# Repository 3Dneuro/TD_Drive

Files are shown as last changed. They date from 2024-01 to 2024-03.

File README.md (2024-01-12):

# TD Drive
Here, we present a novel, 3D-printable implant for rats, named TD Drive, capable of symmetric, bilateral wire electrode recordings, currently in up to six distributed brain areas simultaneously. The open-source design was created employing parametric design principles, allowing prospective users to easily adapt the drive design to their needs by simply adjusting high-level parameters, such as anterior-posterior and medio-lateral coordinates of the recording electrode locations.

We set out to create an easily adjustable hyperdrive to aid neuroscientists in overcoming the difficulties brought about by the multi-area nature of brain interactions. This is one of the main obstacles faced by researchers aiming to exhaustively study the ongoing physiological processes in the brain during both wakefulness and sleep. To capture them accurately, extracellular electrophysiology, recorded with electrodes implanted in the brain areas of interest, is one of methods of choice due to its high temporal resolution and spatial precision.

Classically, studies recording brain activity with extracellular electrodes have employed individual wire electrodes or electrode bundles, such as tetrodes. State-of-the-art probes such as the Neuropixels probe allow the targeting of several areas simultaneously, given that they are aligned on an axis that does allow for implantation of the probe along that axis without impairing the animal. However, accurate simultaneous recordings of multiple, spatially separated areas still remain challenging, with existing methods being either costly or time intensive. 

To make this kind of research more accessible to the scientific community, we set out to create a hyperdrive design that can be modified by individual users, all while being producible in-house. The TD Drive thus aims to overcome some of the drawbacks of existing solutions: it allows targeting of multiple brain areas, mirrored across both hemispheres, with independent wire electrodes simultaneously. Due to its simple design, it can be assembled in a few hours at a relatively low cost. We publish the TD Drive open source, in easily modifiable file formats, to allow researchers to adjust it to their specific needs. A protective cap and electrode interface board (EIB), both available in a standard and enlarged version, complete the experimental framework. The enlarged versions provide increased freedom to make parametric changes to the drive body. Incorporating a parametric 3D modeling approach from the beginning of the TD Drive’s design process allowed us to abstract the parameters necessary to be changed: to change target locations, researchers can simply edit the parameters representing their dorsoventral and anteroposterior coordinates, without the need for redesigning the drive themselves.

Parametric feature demonstration default Parametric feature demonstration alternate

# Parameters
*The parametric design was created in Autodesk Fusion 360. To edit the parameters described below, you will need to import the f3d file into Fusion 360. At time of publication, a free Fusion 360 license for academics/educators was available from Autodesk.*

The TD Drive was designed using a parametric modeling approach. In this process, popular in computer-aided design, different components of the design are linked by interdependent parameters and a defined design history. The design can be altered to suit your needs by modifying the parameters controlling the relevant dimensions. This eliminates the need for researchers to redesign the model themselves, with simple changes to the high-level parameters taking care of all the desired design modifications.

Apart from changing dimensions of the design, the parametric functionality is also used to provide the option to bilaterally add a set of fibers to the body. To make opting in and out of adding the fibers depending on your experimental needs as simple as possible, a custom-made plugin (hyperlink) for Fusion 360 is provided. With use of this plugin, the suppression of all design features pertaining to the fibers can be toggled with the use of a single parameter.

The table below contains the parameter names, a description of their function and some relevant notes regarding their impact on the design. A graphical representation of the parameters for the drive body is available in the form of a drawing that can be found in the design files folder (see preview image below). It  demonstrates the precise, physical dimensions corresponding to the most important parameters (in italics and marked bold in the table as well). This drawing, in combination with the table, can be used to easily visualize and determine what parameters should be modified for the changes that you wish to make.

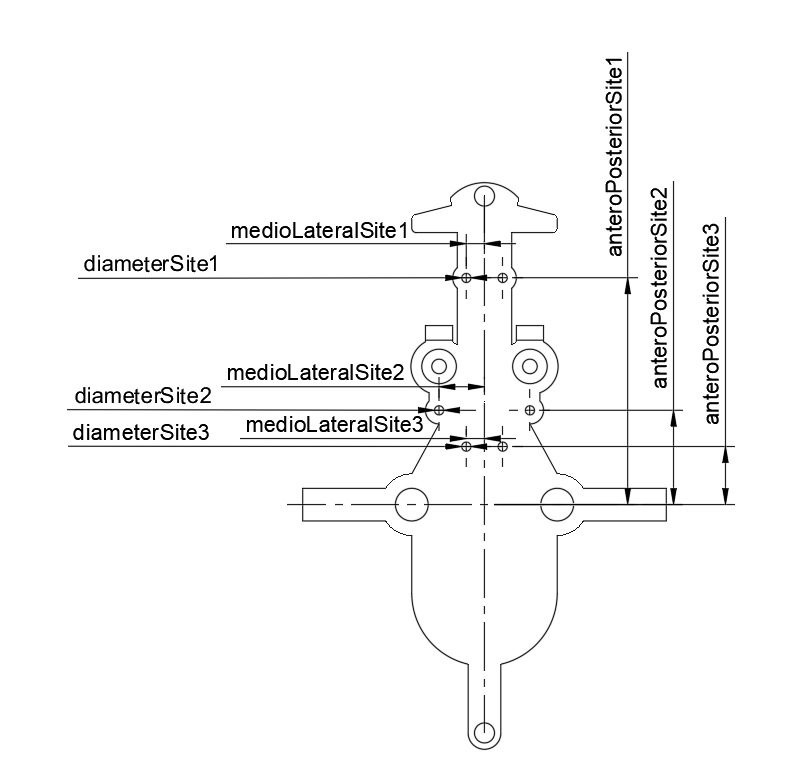
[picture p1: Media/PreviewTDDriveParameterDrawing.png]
Principal parameters drawing


| **Name**                     | **Function**                                                                                                                                                                                     | **Default value** | **Notes**                                                                                                                                  |
|------------------------------|--------------------------------------------------------------------------------------------------------------------------------------------------------------------------------------------------|-------------------|--------------------------------------------------------------------------------------------------------------------------------------------|
| actualMedioLateralSite1      | Defines the definitive mediolateral position of the anterior recording site by checking the target position against the maximum.                                                                 | 1 mm              | if(medioLateralSite1 <= maxMedioLateralSite1; medioLateralSite1; maxMedioLateralSite1)                                                     |
| actualMedioLateralSite2      | Defines the definitive mediolateral position of the medial recording site by checking the target position against the maximum.                                                                   | 2.5 mm            | if(medioLateralSite2 <= maxMedioLateralSite2; medioLateralSite2; maxMedioLateralSite2)                                                     |
| actualMedioLateralSite3      | Defines the definitive mediolateral position of the posterior recording site by checking the target position against the maximum.                                                                | 1 mm              | if(medioLateralSite3 <= maxMedioLateralSite3; medioLateralSite3; maxMedioLateralSite3)                                                     |
| anteroPosteriorFiber         | Adjusts the target anteroposterior distance of the optical fiber holes, taking into account any scaling based on the difference between measured and default bregma-lambda distances.            | 7.7 mm            | ( distanceBregmaLambda + targetAnteroPosteriorFiber ) * ( measuredDistanceBregmaLambda / distanceBregmaLambda )                            |
| **_anteroPosteriorSite1_**   | **_Adjusts the target anteroposterior distance of the anterior recording site, taking into account any scaling based on the difference between measured and default bregma-lambda distances._**  | **_12.5 mm_**     | **_( distanceBregmaLambda + targetAnteroPosteriorSite1 ) * ( measuredDistanceBregmaLambda / distanceBregmaLambda )_**                      |
| **_anteroPosteriorSite2_**   | **_Adjusts the target anteroposterior distance of the medial recording site, taking into account any scaling based on the difference between measured and default bregma-lambda distances._**    | **_5.2 mm_**      | **_( distanceBregmaLambda + targetAnteroPosteriorSite2 ) * ( measuredDistanceBregmaLambda / distanceBregmaLambda )_**                      |
| **_anteroPosteriorSite3_**   | **_Adjusts the target anteroposterior distance of the posterior recording site, taking into account any scaling based on the difference between measured and default bregma-lambda distances._** | **_3.2 mm_**      | **_( distanceBregmaLambda + targetAnteroPosteriorSite3 ) * ( measuredDistanceBregmaLambda / distanceBregmaLambda )_**                      |
| diameterBrassInsert          | Controls the diameter of the hole reserved for the brass insert of the shuttle assembly to lower into.                                                                                           | 1.9 mm            |                                                                                                                                            |
| diameterEIBScrew             | Controls the diameter of the holes used to join the drive body to the EIB.                                                                                                                       | 1.8 mm            |                                                                                                                                            |
| diameterShuttleScrewMajor    | Controls the major diameter of the cover for the shuttle screw.                                                                                                                                  | 0.9 mm            |                                                                                                                                            |
| diameterShuttleScrewMinor    | Controls the minor diameter of the cover for the shuttle screw.                                                                                                                                  | 0.8 mm            |                                                                                                                                            |
| **_diameterSite1_**          | **_Controls the diameter of the most anterior recording site._**                                                                                                                                 | **_0.5 mm_**      |                                                                                                                                            |
| **_diameterSite2_**          | **_Controls the diameter of the most medial recording site._**                                                                                                                                   | **_0.5 mm_**      |                                                                                                                                            |
| **_diameterSite3_**          | **_Controls the diameter of most posterior recording site._**                                                                                                                                    | **_0.5 mm_**      |                                                                                                                                            |
| distanceBregmaLambda         | Controls the distance between the projected Bregma and Lambda points.                                                                                                                            | 9 mm              |                                                                                                                                            |
| distanceFrontBackEIBHoles    | Controls the distance between the front and back screw holes used to possibly further join the drive body and EIB.                                                                               | 29.601 mm         | These holes are currently not in use for fastening the EIB, the larger more medial holes are sufficient.                                   |
| distanceMedioLateralEIBHoles | Controls the mediolateral distance of the EIB screw holes.                                                                                                                                       | 4 mm              | With respect to the midline.                                                                                                               |
| heightShuttleGuide           | Controls the height to which the shuttle guide extends above the top surface of the body.                                                                                                        | 8.2 mm            | thicknessDriveBodyTop + 6 mm                                                                                                               |
| lengthBackPedestals          | Controls the length of the supporting pedestals where the polyamide screws for the EIB thread into.                                                                                              | 15.2 mm           |                                                                                                                                            |
| lengthShuttleScrew           | Controls the length of the cover of the movable shuttle assembly.                                                                                                                                | 15.2 mm           |                                                                                                                                            |
| maxMedioLateralSite1         | Controls the maximum mediolateral position of the anterior recording site.                                                                                                                       | 2 mm              | It is not recommended to alter these maximum limits, interactions between model features can fail when pushing beyond the default limits.  |
| maxMedioLateralSite2         | Controls the maximum mediolateral position of the medial recording site.                                                                                                                         | 5 mm              | It is not recommended to alter these maximum limits, interactions between model features can fail when pushing beyond the default limits.  |
| maxMedioLateralSite3         | Controls the maximum mediolateral position of the posterior recording site.                                                                                                                      | 2 mm              | It is not recommended to alter these maximum limits, interactions between model features can fail when pushing beyond the default limits.  |
| measuredDistanceBregmaLambda | Sets the individually measured bregma-lambda distances to be used for scaling the final positions to ensure accuracy.                                                                            | 9 mm              | This value is used in scaling calculations of the final position, set it to 9 mm (distance used in designing) to disable scaling.          |
| medioLateralFiber            | Controls the mediolateral distance of the optical fiber holes.                                                                                                                                   | 1 mm              | Change this parameter to your intended position with respect to the midline.                                                               |
| **_medioLateralSite1_**      | **_Controls the mediolateral distance of the most anterior recording site._**                                                                                                                    | **_1 mm_**        | **_Change this parameter to your intended position with respect to the midline. The maximum limits will automatically be applied._**       |
| **_medioLateralSite2_**      | **_Controls the mediolateral distance of the most medial recording site._**                                                                                                                      | **_2.5 mm_**      | **_Change this parameter to your intended position with respect to the midline. The maximum limits will automatically be applied._**       |
| **_medioLateralSite3_**      | **_Controls the mediolateral distance of the most posterior recording site._**                                                                                                                   | **_1 mm_**        | **_Change this parameter to your intended position with respect to the midline. The maximum limits will automatically be applied._**       |
| supressFiber                 | Provides the interface with the API script to control suppression of all features pertaining to the optical fiber holes.                                                                         | 0                 | After setting either a value of 0 or 1, the corresponding Fusion 360 API script should be run to actuate the suppression.                  |
| tapDepth                     | Controls the length of the shuttle screw cover that will be tapped in post-production.                                                                                                           | 3.9 mm            |                                                                                                                                            |
| targetAnteroPosteriorFiber   | Sets the target anteroposterior position of the optical fiber holes with respect to bregma.                                                                                                      | -1.3 mm           | Change this parameter to your intended position and any scaling and maximum limit calculations will be performed and applied to the model. |
| targetAnteroPosteriorSite1   | Sets the target anteroposterior position of the anterior recording site with respect to bregma.                                                                                                  | 3.5 mm            | Change this parameter to your intended position and any scaling and maximum limit calculations will be performed and applied to the model. |
| targetAnteroPosteriorSite2   | Sets the target anteroposterior position of the medial recording site with respect to bregma.                                                                                                    | -3.8 mm           | Change this parameter to your intended position and any scaling and maximum limit calculations will be performed and applied to the model. |
| targetAnteroPosteriorSite3   | Sets the target anteroposterior position of the posterior recording site with respect to bregma.                                                                                                 | -5.8 mm           | Change this parameter to your intended position and any scaling and maximum limit calculations will be performed and applied to the model. |
| thicknessDriveBodyBottom     | Controls the thickness of the bottom section of the drive body.                                                                                                                                  | 0.8 mm            |                                                                                                                                            |
| thicknessDriveBodyTop        | Controls the thickness of the top section of the drive body.                                                                                                                                     | 2.2 mm            |                                                                                                                                            |

# Manufacturing
With the open-source availability of all the relevant files for our hyperdrive framework, all parts can be made in-house. The drive body and cap components can be 3D printed while the custom EIB requires dedicated printed circuit board (PCB) production facilities. When not in possession of adequate equipment or skills, the production can be outsourced to dedicated companies using the available files. We acquire the EIBs externally and print all cap components and the hyperdrive bodies using a commercially available high-resolution 3D printer. Printing of the bodies is occasionally outsourced to specialized services to ensure quality whenever desired or required.

# Assembly
A number of post-processing and assembly steps are needed before the drive can be used in experiments. A detailed protocol is available on request. Please contact contact@3dneuro.com for further details. This protocol can be used as a guide for the complete assembly process to ensure the successful production of TD Drives.

Assembled TD Drive

# License
Copyright 3Dneuro 2022. This source describes Open Hardware and is licensed under the CERN-OHL-S v2 You may redistribute and modify this documentation and make products using it under the terms of the CERN-OHL-S v2 (https:/cern.ch/cern-ohl). This documentation is distributed WITHOUT ANY EXPRESS OR IMPLIED WARRANTY, INCLUDING OF MERCHANTABILITY, SATISFACTORY QUALITY AND FITNESS FOR A PARTICULAR PURPOSE. Please see the CERN-OHL-S v2 for applicable conditions. Source location: https://www.3dneuro.com/open-hardware/ https://choosealicense.com/licenses/cern-ohl-s-2.0/

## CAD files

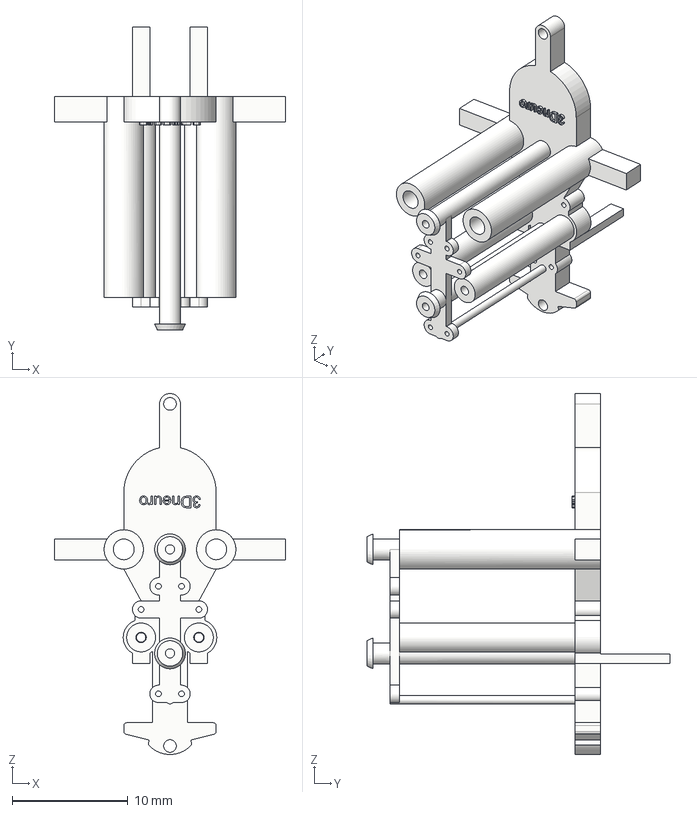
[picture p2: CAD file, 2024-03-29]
Design files/STEP/Parametric TD Drive Body.step
20.0 x 26.2 x 31.2 mm

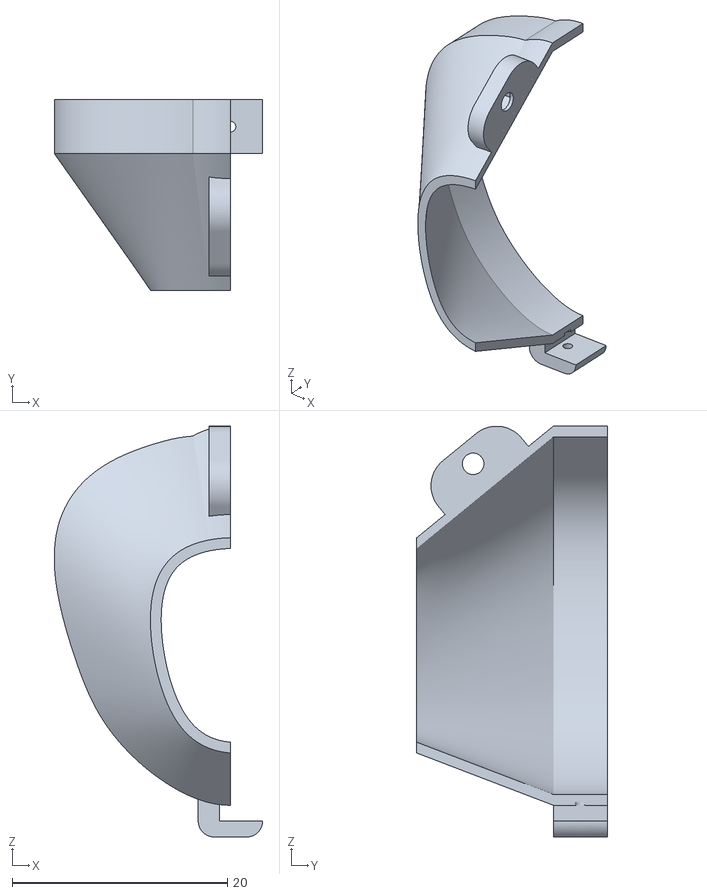
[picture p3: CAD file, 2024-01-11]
Design files/STL/Parametric Cap Left Side.stl
19.4 x 17.7 x 38.2

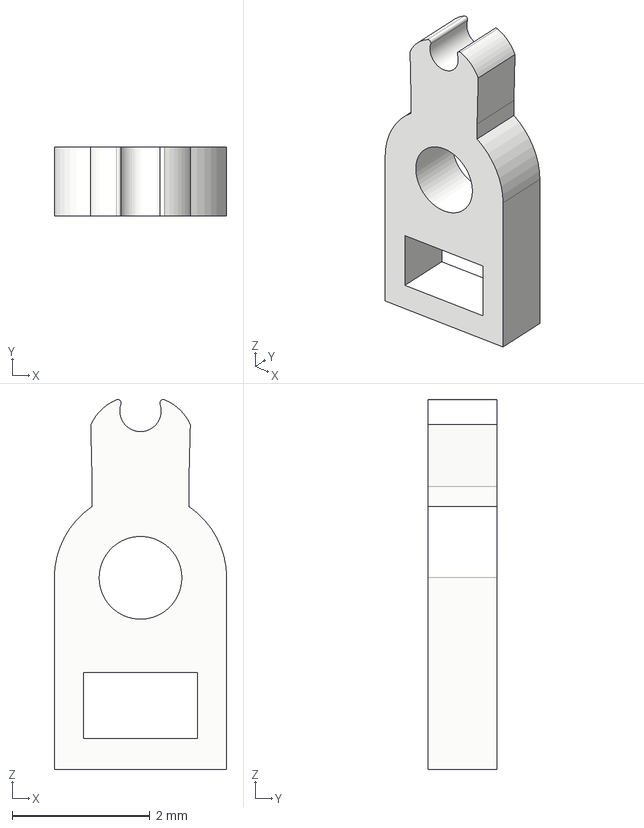
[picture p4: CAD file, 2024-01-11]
Design files/STEP/TD Drive Shuttle.step
2.50 x 1.00 x 5.37 mm

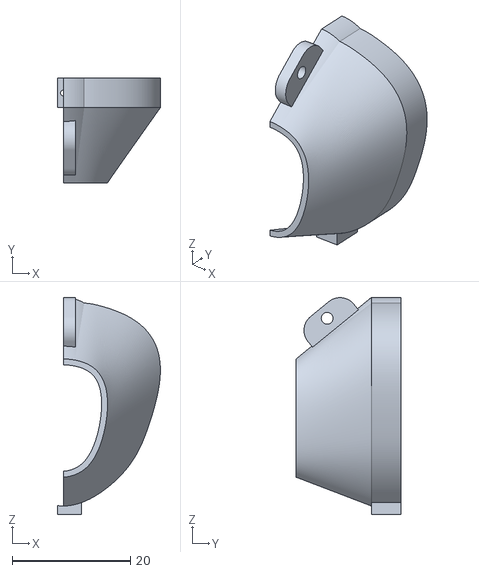
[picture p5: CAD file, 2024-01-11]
Design files/STL/Parametric Cap Right Side.stl
17.4 x 17.7 x 36.7

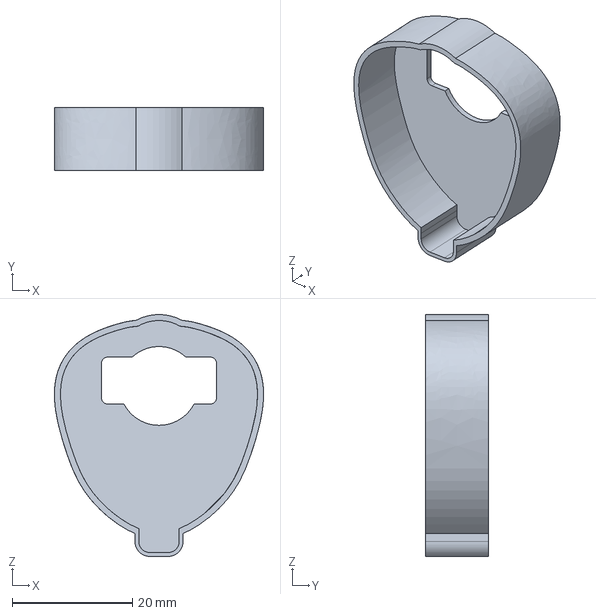
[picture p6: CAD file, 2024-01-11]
Design files/STEP/Parametric Recording Cap.step
34.7 x 10.5 x 40.2 mm

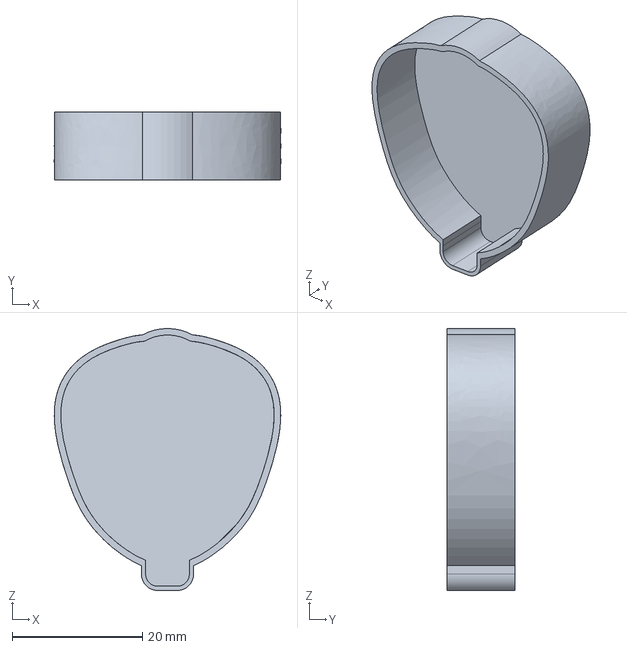
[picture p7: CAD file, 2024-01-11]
Design files/STEP/Parametric Cap.step
34.7 x 10.5 x 40.2 mm

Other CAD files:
Design files/STEP/Parametric Cap Right.step
Design files/STEP/Parametric Cap Left.step
Design files/Fusion 360/Parametric Cap Left.f3d
Design files/Fusion 360/Parametric Cap Right.f3d
Design files/Fusion 360/Parametric Cap.f3d
Design files/Fusion 360/Parametric Recording Cap.f3d
Design files/Fusion 360/Parametric TD Drive Body.f3d
Design files/Fusion 360/TD Drive Shuttle.f3d
Design files/STL/Parametric Cap.stl
Design files/STL/Parametric Recording Cap.stl
Design files/STL/Parametric TD Drive Body.stl
Design files/STL/TD Drive Shuttle.stl

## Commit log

2024-01-11 Organize into folder
    [Parametric Cap Left.f3d]
2024-01-11 Rename Parametric Cap.f3d to Design files/Fusion 360/Parametric Cap.f3d
    [Parametric Cap.f3d]
2024-01-11 Parametric Cap.f3d
    [Parametric Recording Cap.f3d]
